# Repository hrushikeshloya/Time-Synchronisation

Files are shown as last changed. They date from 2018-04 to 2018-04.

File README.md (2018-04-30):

# EDL-TimeSync
Public Repository of our Electronic Design Lab Project Time Synchronization in Vibration Sensors under Prof. M.C. Chandorkar

Members:
1. Hrushikesh Loya (150010017@iitb.ac.in)
2. Rajat Patel (150010002@iitb.ac.in)
3. Yashswi Jain (150110039@iitb.ac.in)

### About

The project attempts to build a customizable skeleton which can be used to synchronise multiple sensors to take time stamped readings and transmit it to the user. 

We have developed a skeleton that can accommodate two vibration sensors (MMA7361, in our case) mounted on two self-designed and realised peripheral microcontrollers with ATMEGA-328P and a customised central Microprocessor for collecting the sampled and stamped data from both of them and sending them them to the UNIX PC for further analysis. 

### Board Design

You can find the eagle schematic and board files for both the central and peripheral microcontroller in Board Design folder.

### Communication Protocols

#### Mode 1 (CSS)
Continuous Sampling and Sending: The sampled data is sent to PC by each of the two Local Microprocessors alternatively. The sampling is done through interrupts and time spent in each interrupt service routine as mentioned above is 35 microseconds. This doesn’t affect the transmission as ATMEGA328p has 64 byte buffer for Serial transmission.
Maximum Attainable sampling rate: 2.5KHz

#### Mode 2 (Burst Mode)
Sampling till buffer is full and then sending in a burst: In this method we sample the data till the buffer is full and then send the data from 2 Local Microprocessors to the PC alternatively. The sampling of Data is stopped when the data is transmitted to PC. The sampling starts only after both the Local Microprocessors are done with the transmission.
Maximum Attainable sampling rate: 25KHz

### Time Synchronization

As the two peripheral microcontrollers have different clocks, there will be drifts in both the clocks after some time. To match the sampling instants, we use the same square wave which we sent from central for alternate data sending.

If there is drift in clocks, the timer1 (inbuilt timer in Atmega328P) values will not be same. So after certain number of cycles of square wave we set the the timer1 values of both the  microprocessors to initial values. And we send the timestamp when the synchronization is done to PC from Central Microprocessor. This way we acheive synchronized data.

### Firmware

##### How to upload the code?
Use Arduino IDE, to compile and upload the code. central.ino corresponds to central microprocessor, interrupt_transmit.ino corresponds to first peripheral, and interrupt_transmit2.ino corresponds to second peripheral.

##### Aquiring Serial Data on PC?
We use picocom (sudo apt-get install picocom) to aquire the serial data on ubuntu based PC. 
sudo picocom -b 230400 /dev/ttyUSB0 | tee logfile  (check your port on which arduino is connected, our case it was /dev/ttyUSB0)  saves the data from the serial port of the computer to a log file named logfile.

##### Plotting and Interpretting the data?
The data we recieve is in byte format.
You can then use log_reader_v1.py and log_reader_v2.py to plot the data aquired without time sync and with timesync respectively.

### Results

You can have a view of few of the amazing results (with their log files) we have obtained in the Results folder

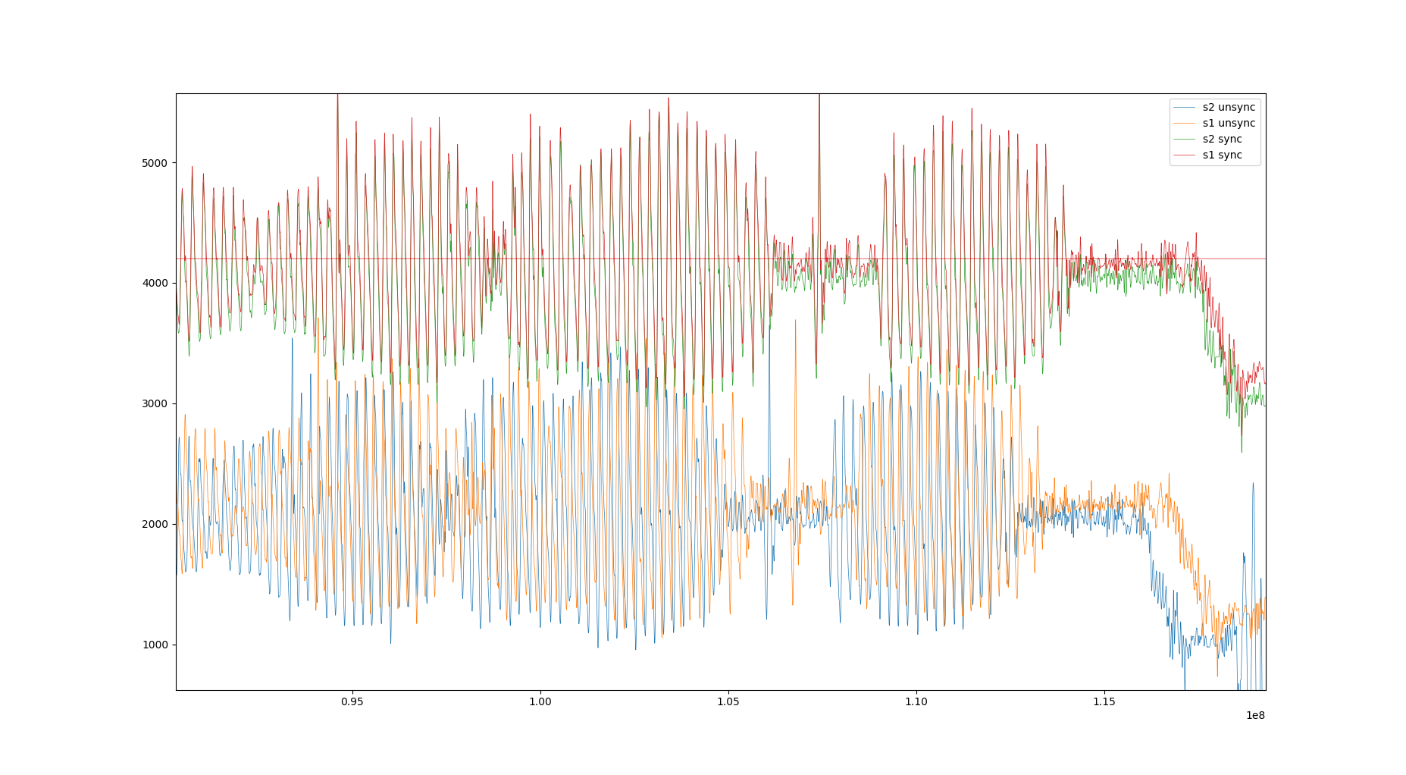
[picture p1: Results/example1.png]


Link to our complete report: https://docs.google.com/document/d/1JRsnFTGfe37P0LFT0vE4qM5fWR5oT6ynj_dwdIWIZMQ/edit?usp=sharing

Link to the final presenentation: https://docs.google.com/presentation/d/1-vB_suMupCKIn_ZJjNBb9ri4n2t6BEERArDRMrE7F0k/edit?usp=sharing

Refrences: 

1. "Time synchronization of a wired sensor network for structural health monitoring":  http://iopscience.iop.org/article/10.1088/0964-1726/17/01/015016

Chalte Hai!

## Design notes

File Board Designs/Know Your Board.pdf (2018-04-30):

# P_P- Peripheral & P_P - Central

### 1. Powering Up

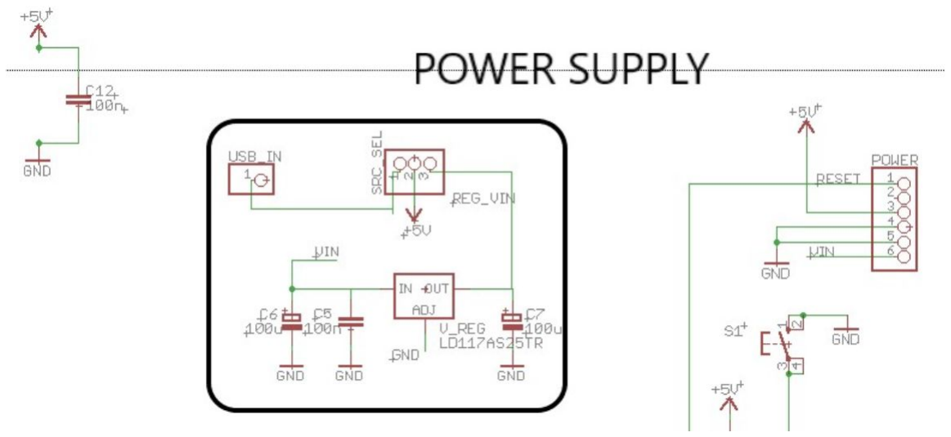
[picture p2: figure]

In the Figure above, the 6X1 pin-head on the right corner is the Power Section of the board. V-In and +5V pins can be found here.

The Board has a dual channel powering mechanism.
- Using the USB_VCC : If you plan to use your peripheral attached with a FTDI module which is capable of harnessing the USB_VCC then all you need to do is plug in the USB_VCC directly into any of the +5V pins on the board to power it up.
- Using External Power Supply : The board can also be powered
externally by a 10V DC | supply. The Input can be given to the V-IN | pin
in power section of the board and the Regulated 5V output (REG_VIN) has to be connected to +5V pin manually with a jumper.
For regulating the voltage, the board houses a LD1117 LDO voltage regulator at its heart.

Checking the power supply:
Power up the board using any one of the two sources as described above. If everything is correct, A RED LED will start glowing. This indicates that the Power unit of the Board is working fine.

### 2. Atmega 328P Pins at your Disposal

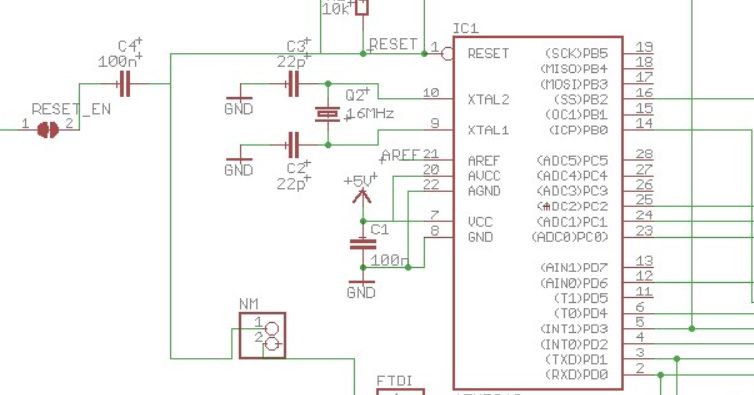
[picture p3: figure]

| The Board houses a 16MHz | crystal oscillator. With an appropriate prescaling factor(We
have used a factor of 4). At this prescaling factor, a max sampling frequency of around 320 KHz can be attained using the board.

The figure shows the Accelerometer of the board. This can be used to interface the board with a MMA7361 Triple - Axis accelerometer. (Its a P_P-Peripheral ONLY feature)

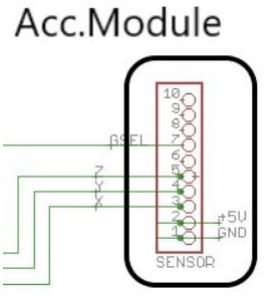
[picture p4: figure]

For detailed pin layout please refer to the Peripheral2.sch file.

CAUTION: It hasn’t been shown in the figure or the Schematic but the updated version of the board also comprises pins for Self-test, sleep and Sensitivity select. It should be clear from the labelling of the pins on the board.

FTDI Interfacing:

The figure shows the Pin head which can be used for interfacing the FTDI module.

ATTENTION: The NM pinhead has to be left unconnected!

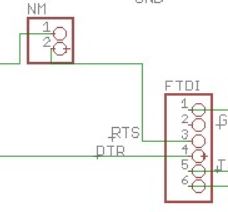
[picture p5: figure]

Communication Pins:

- P_P-Central

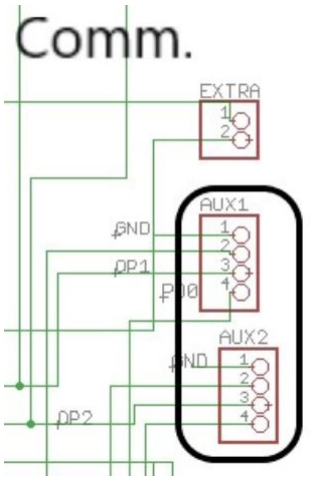
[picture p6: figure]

The figure shows the Communication front of the central microprocessor.
The EXTRA titled pinhead lets the user the freedom to use 1 analog and 1 digital pin by his own will(Unassigned pins)

AUX1 and AUX2 respectively is used for communicating with the auxiliary microprocessors. Each comprises of a GND pin, RX-TX pins and one digital pin.

OP1 - Atmega PIN 12 (dig.)
OP2 - Atmega PIN 6 (dig.)

- P_P- Peripheral:

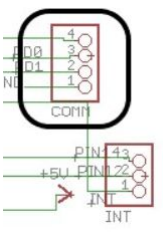
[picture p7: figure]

The figure shows the pinhead for communication with
the central microprocessor.
The COMM. pinhead is used for communication. The INT. pinhead houses 3 extra digital pins if required. (atmega pin 4,12,14).

The COMM. Pinhead comprises of RX,TX pins, 1 Dig. Pin (Pin 5 of ATMEGA), and GND. pin

Switches:

Both the boards have two switches each. One of them is used for resetting the microcontroller and the other is used for giving a high pulse at one of the digital pins of the atmega.

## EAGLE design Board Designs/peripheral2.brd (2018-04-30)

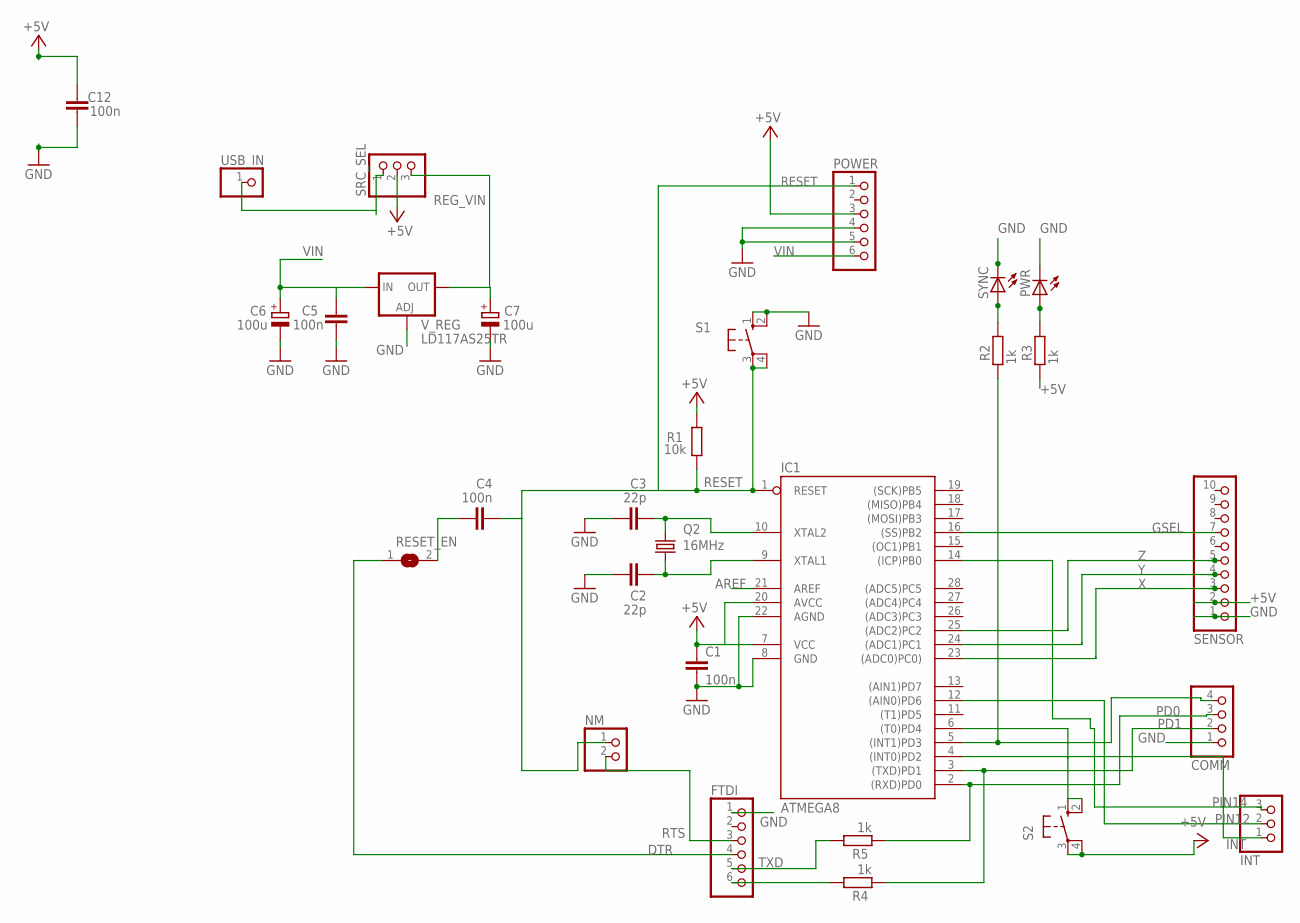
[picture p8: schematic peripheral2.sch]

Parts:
C1, C4, C5, C12: 100n; C1206
C2, C3: 22p; C1206
C6, C7: 100u; PANASONIC_D
COMM: PINHD-1X4; 1X04
FTDI: PINHD-1X6; 1X06
IC1: ATMEGA8; DIL28-3
INT: PINHD-1X3; 1X03
NM: PINHD-1X2; 1X02
POWER: PINHD-1X6; 1X06
PWR: LEDCHIPLED_1206; CHIPLED_1206
Q2: 16MHz; HC49/S
R1: 10k; R1206
R2, R3, R4, R5: 1k; R1206
RESET_EN: SJ
S1, S2: 10-XX; B3F-10XX
SENSOR: PINHD-1X10; 1X10
SRC_SEL: PINHD-1X3; 1X03
SYNC: LEDCHIPLED_1206; CHIPLED_1206
USB_IN: PINHD-1X1; 1X01
V_REG: LD117AS25TR; SOT223

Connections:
+5V: C1.1, C12.2, IC1.7 (VCC), IC1.20 (AVCC), POWER.3, R1.2, R3.2, S2.3, S2.4 (P1), SENSOR.2, SRC_SEL.2
A3: COMM.4, IC1.5 ((INT1)PD3), R2.2
AREF: IC1.21 (AREF)
DTR: FTDI.4, RESET_EN.1
GND: C1.2, C2.1, C3.1, C5.1, C6.-, C7.-, C12.1, COMM.1, FTDI.1, IC1.8 (GND), IC1.22 (AGND), POWER.4, POWER.5, PWR.C, S1.1 (S), S1.2 (S1), SENSOR.1, SYNC.C, V_REG.1 (ADJ)
GSEL: IC1.16 ((SS)PB2), SENSOR.7
INT: IC1.4 ((INT0)PD2), INT.1
unnamed: R2.1, SYNC.A
unnamed: PWR.A, R3.1
unnamed: FTDI.6, R4.1
unnamed: C2.2, IC1.9 (XTAL1), Q2.1
unnamed: C3.2, IC1.10 (XTAL2), Q2.2
unnamed: IC1.6 ((T0)PD4), S2.1 (S), S2.2 (S1)
unnamed: C4.1, RESET_EN.2
PD0: COMM.3, IC1.2 ((RXD)PD0), R5.2
PD1: COMM.2, IC1.3 ((TXD)PD1), R4.2
PIN12: IC1.12 ((AIN0)PD6), INT.2
PIN14: IC1.14 ((ICP)PB0), INT.3
REG_VIN: C7.+, SRC_SEL.3, V_REG.4 (OUT)
RESET: C4.2, IC1.1 (RESET), NM.1, POWER.1, R1.1, S1.3, S1.4 (P1)
RTS: FTDI.3, NM.2
TXD: FTDI.5, R5.1
USB_VCC: SRC_SEL.1, USB_IN.1
VIN: C5.2, C6.+, POWER.6, V_REG.3 (IN)
X: IC1.23 ((ADC0)PC0)), SENSOR.3
Y: IC1.24 ((ADC1)PC1), SENSOR.4
Z: IC1.25 ((ADC2)PC2), SENSOR.5

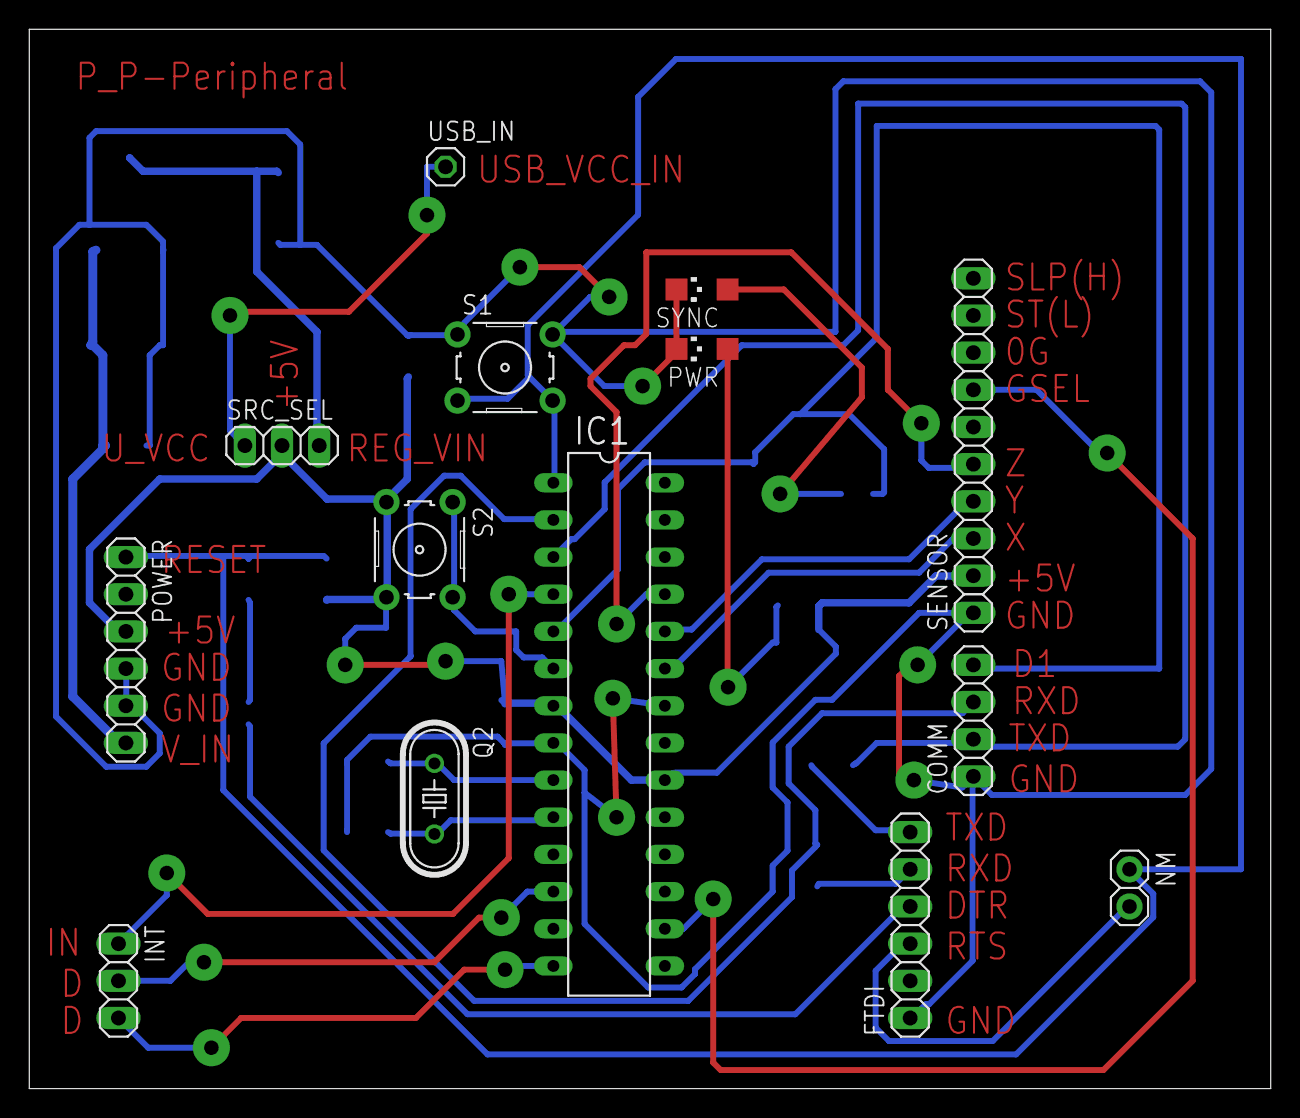
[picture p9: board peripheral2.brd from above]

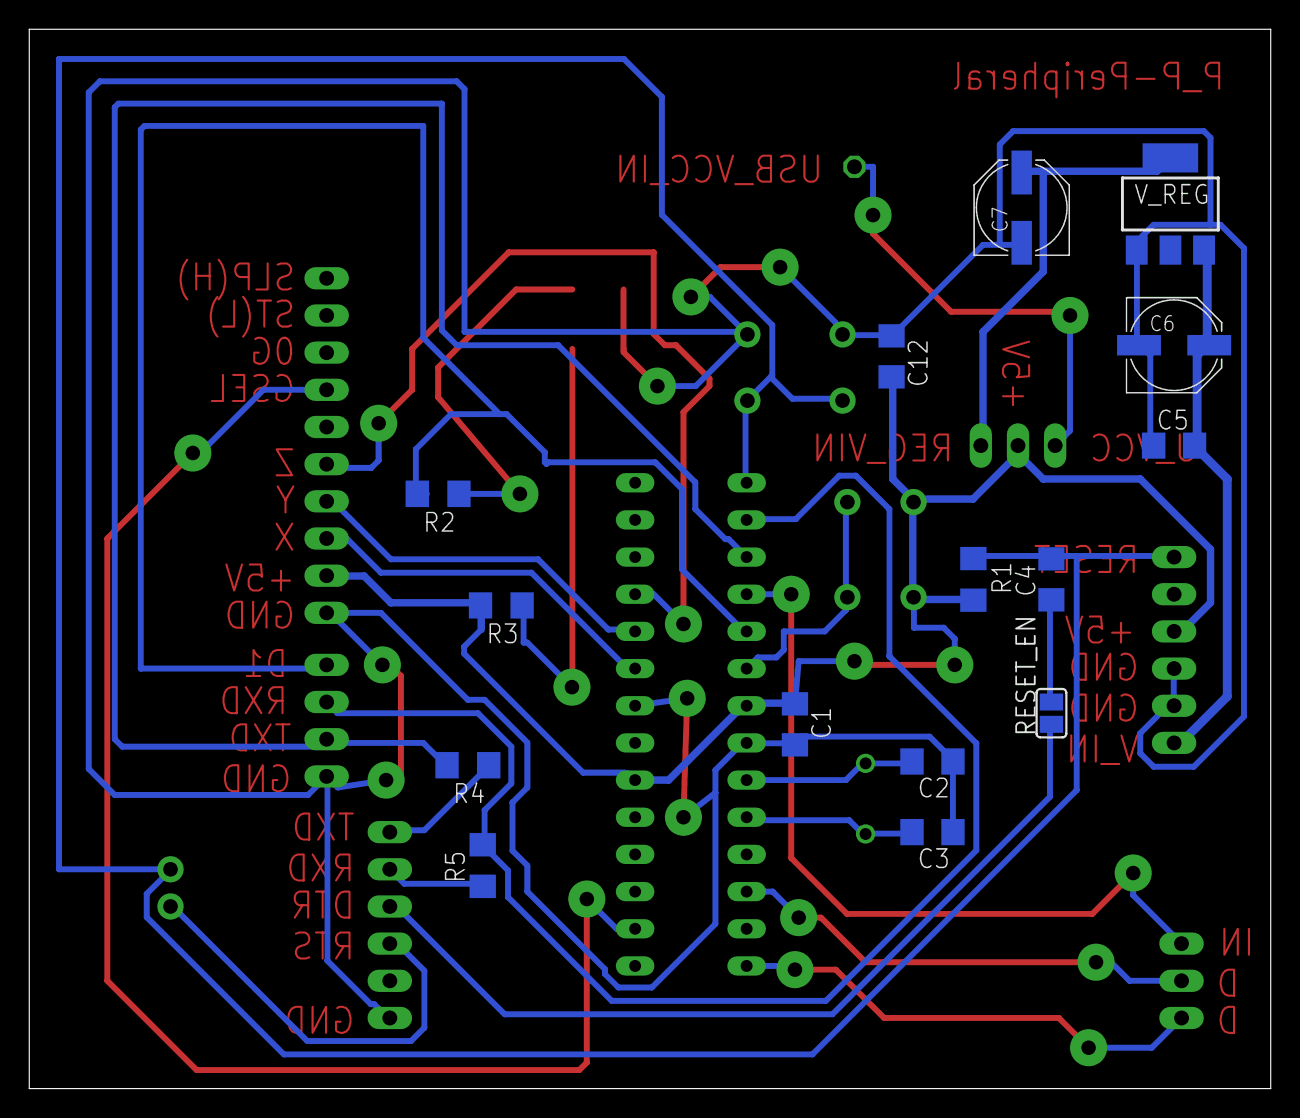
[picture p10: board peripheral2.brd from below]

Board: 2 copper layers, 84.8 x 72.4 mm, 29 parts (15 on the bottom side), 26 nets.

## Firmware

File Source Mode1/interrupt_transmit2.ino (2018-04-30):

#ifndef AcceleroMMA7361_h
#define AcceleroMMA7361_h
#define cbi(sfr, bit) (_SFR_BYTE(sfr) &= ~_BV(bit))
#define sbi(sfr, bit) (_SFR_BYTE(sfr) |= _BV(bit))
#if defined(ARDUINO) && ARDUINO >= 100
#include <Arduino.h>
#else
#include <WProgram.h>
#include <pins_arduino.h>
#endif

class AcceleroMMA7361
{
  public:
    AcceleroMMA7361();
    void begin();
    void begin(int sleepPin, int selfTestPin, int zeroGPin, int gSelectPin, int xPin, int yPin, int zPin);
    int getXRaw();
    int getYRaw();
    int getZRaw();
    int getXVolt();
    int getYVolt();
    int getZVolt();
    int getXAccel();
    int getYAccel();
    int getZAccel();
    void getAccelXYZ(int *_XAxis, int *_YAxis, int *_ZAxis);
    int getTotalVector();
    void setOffSets(int xOffSet, int yOffSet, int zOffSet);
    void calibrate();                             // only to be executed when Z-axis is oriented to the ground
// it calculates the offset values by assuming  Z = +1 G ; X and Y  = 0 G
    void setARefVoltage(double _refV);
    void setAveraging(int avg);
    int getOrientation();
    void setSensitivity(boolean sensi);
    void sleep();
    void wake();
    int _mapMMA7361V(int value);
    int _mapMMA7361G(int value);
        int _offSets[3];

  private:

    int _sleepPin;
    int _selfTestPin;
    int _zeroGPin;
    int _gSelectPin;
    int _xPin;
    int _yPin;
    int _zPin;

    int _polarities[3];
    double _refVoltage;
    int _average;
    boolean _sleep;
    boolean _sensi;
};
#endif



// acceleroMMA7361.h - Library for retrieving data from the MMA7361 accelerometer. 
// Copyright 2011-2012 Jef Neefs (neefs@gmail.com) and Jeroen Doggen (jeroendoggen@gmail.com)
// For more information: variable declaration, changelog,... see AcceleroMMA7361.h 
//
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
/// acceleroMMA7361.cpp - Library for retrieving data from the MMA7361 accelerometer.
/// For more information: variable declaration, changelog,... see AcceleroMMA7361.h


/// constructor
AcceleroMMA7361::AcceleroMMA7361()
{
    _sleepPin=0;
    _selfTestPin=0;
    _zeroGPin=0;
    _gSelectPin=0;
    _xPin=0;
    _yPin=0;
    _zPin=0;
    _offSets[0]=0;
    _offSets[1]=0;
    _offSets[2]=0;
    _polarities[0]=0;
    _polarities[1]=0;
    _polarities[2]=0;
    _refVoltage=0;
    _average=0;
    _sleep=false;
    _sensi=false;
}

/// begin function to set pins: sleepPin = 13, selfTestPin = 12, zeroGPin = 11, gSelectPin = 10, xPin = A0, yPin = A1, zPin = A2.
/// When you use begin() with an empty parameter list, these standard values are used
void AcceleroMMA7361::begin()
{
  begin(13, 12, 11, 10, A0, A1, A2);
}

/// begin variables
/// - int sleepPin: number indicating to which pin the sleep port is attached. DIGITAL OUT
/// - int selfTestPin: number indicating to which pin the selftest port is attached. DIGITAL OUT
/// - int zeroGPin: number indicating to which pin the ZeroGpin is connected to. DIGITAL IN
/// - int gSelectPin: number indication to which pin the Gselect is connected to. DIGITAL OUT
/// - int xPin: number indicating to which pin the x-axis pin is connected to. ANALOG IN
/// - int yPin: number indicating to which pin the y-axis  pin is connected to. ANALOG IN
/// - int zPin: number indicating to which pin the z-axis  pin is connected to. ANALOG IN
/// - int offset: array indicating the G offset on the x,y and z-axis
/// When you use begin() without variables standard values are loaded: A0,A1,A2 as input for X,Y,Z and digital pins 13,12,11,10 for sleep, selftest, zeroG and gSelect
void AcceleroMMA7361::begin(int sleepPin, int selfTestPin, int zeroGPin, int gSelectPin, int xPin, int yPin, int zPin)
{
  pinMode(sleepPin, OUTPUT);
  pinMode(selfTestPin, OUTPUT);
  pinMode(zeroGPin, INPUT);
  pinMode(gSelectPin, OUTPUT);
  pinMode(xPin, INPUT);
  pinMode(yPin, INPUT);
  pinMode(zPin, INPUT);
  digitalWrite(sleepPin,HIGH);
  digitalWrite(selfTestPin,LOW);
  _sleepPin = sleepPin;
  _selfTestPin = selfTestPin;
  _zeroGPin = zeroGPin;
  _gSelectPin = gSelectPin;
  _xPin = xPin;
  _yPin = yPin;
  _zPin = zPin;
  _sleep = false;
  setOffSets(0,0,0);
  setARefVoltage(5);
  setAveraging(10);
  setSensitivity(HIGH);
}

/// setOffSets( int offSetX, int offSetY, int offSetZ): Sets the offset values for the x,y,z axis.
/// The parameters are the offsets expressed in G-force (100 = 1 G)
/// Offsets are added to the raw datafunctions
void AcceleroMMA7361::setOffSets(int xOffSet, int yOffSet, int zOffSet)
{
  if (_refVoltage==3.3)
  {
    _offSets[0]= map(xOffSet,0,3300,0,1024);
    _offSets[1]= map(yOffSet,0,3300,0,1024);
    _offSets[2]= map(zOffSet,0,3300,0,1024);
  }
  else
  {
    _offSets[0]= map(xOffSet,0,5000,0,1024);
    _offSets[1]= map(yOffSet,0,5000,0,1024);
    _offSets[2]= map(zOffSet,0,5000,0,1024);
  }
}

/// setARefVoltage(double _refV): Sets the AREF voltage to external, (now only takes 3.3 or 5 as parameter)
/// default is 5 when no AREF is used. When you want to use 3.3 AREF, put a wire between the AREF pin and the
/// 3.3 V VCC pin. This increases accuracy
void AcceleroMMA7361::setARefVoltage(double refV)
{
  _refVoltage = refV;
  if (refV == 3.3)
  {
    analogReference(EXTERNAL);
  }
}

/// setAveraging(int avg): Sets how many samples have to be averaged in getAccel default is 10.
void AcceleroMMA7361::setAveraging(int avg)
{
  _average = avg;
}

/// setSensitivity sets the sensitivity to +/-1.5 G (HIGH) or +/-6 G (LOW) using a boolean HIGH (1.5 G) or LOW (6 G)
void AcceleroMMA7361::setSensitivity(boolean sensi)
{
  _sensi = sensi;
  digitalWrite(_gSelectPin, !sensi);
}

/// sleep lets the device sleep (when device is sleeping already this does nothing)
void AcceleroMMA7361::sleep()
{
  if (!_sleep)
  {
    digitalWrite(_sleepPin, LOW);
    _sleep = true;
  }
}

/// wake enables the device after sleep (when device is not sleeping this does nothing) there is a 2 ms delay, due to enable response time (datasheet: typ 0.5 ms, max 2 ms)
void AcceleroMMA7361::wake()
{
  if (_sleep == true)
  {
    digitalWrite(_sleepPin, HIGH);
    _sleep = false;
    delay(2);
  }
}

/// getXRaw(): Returns the raw data from the X-axis analog I/O port of the Arduino as an integer
int AcceleroMMA7361::getXRaw()
{
  return analogRead(_xPin)+_offSets[0]+2;
}

/// getYRaw(): Returns the raw data from the Y-axis analog I/O port of the Arduino as an integer
int AcceleroMMA7361::getYRaw()
{
  return analogRead(_yPin)+_offSets[1]+2;
}

/// getZRaw(): Returns the raw data from the Z-axis analog I/O port of the Arduino as an integer
int AcceleroMMA7361::getZRaw()
{
  return analogRead(_zPin)+_offSets[2];
}

/// getXVolt(): Returns the voltage in mV from the X-axis analog I/O port of the Arduino as a integer
int AcceleroMMA7361::getXVolt()
{
  return _mapMMA7361V(getXRaw());
}

/// getYVolt(): Returns the voltage in mV from the Y-axis analog I/O port of the Arduino as a integer
int AcceleroMMA7361::getYVolt()
{
  return _mapMMA7361V(getYRaw());
}

/// getZVolt(): Returns the voltage in mV from the Z-axis analog I/O port of the Arduino as a integer
int AcceleroMMA7361::getZVolt()
{
  return _mapMMA7361V(getZRaw());
}

/// getXAccel(): Returns the acceleration of the X-axis as a int (1 G = 100.00)
int AcceleroMMA7361::getXAccel()
{
   return _mapMMA7361G(getXRaw());
}

/// getYAccel(): Returns the acceleration of the Y-axis as a int (1 G = 100.00)
int AcceleroMMA7361::getYAccel()
{
  
  return _mapMMA7361G(getYRaw());
}

/// getZAccel(): Returns the acceleration of the Z-axis as a int (1 G = 100.00)
int AcceleroMMA7361::getZAccel()
{
 return _mapMMA7361G(getZRaw());
}

/// getAccelXYZ(int *_XAxis, int *_YAxis, int *_ZAxis) returns all axis at once as pointers
void AcceleroMMA7361::getAccelXYZ(int *_XAxis, int *_YAxis, int *_ZAxis)
{
  int sum[3];
  sum[0] = 0;
  sum[1] = 0;
  sum[2] = 0;
  for (int i = 0;i<_average;i++)
  {
    sum[0] = sum[0] + _mapMMA7361G(getXRaw());
    sum[1] = sum[1] + _mapMMA7361G(getYRaw());
    sum[2] = sum[2] + _mapMMA7361G(getZRaw());
  }
  *_XAxis = sum[0]/_average;
  *_YAxis = sum[1]/_average;
  *_ZAxis = sum[2]/_average;
}

/// mapMMA7361V: calculates and returns the voltage value derived from the raw data. Used in getXVoltage, getYVoltage, getZVoltage
int AcceleroMMA7361::_mapMMA7361V(int value)
{
  if (_refVoltage==3.3)
  {
    return map(value,0,1024,0,3300);
  }
  else
  {
    return map(value,0,1024,0,5000);
  }
}

/// mapMMA7361G: calculates and returns the accelerometer value in degrees derived from the raw data. Used in getXAccel, getYAccel, getZAccel
int AcceleroMMA7361::_mapMMA7361G(int value)
{
  if(_sensi == false)
  {
    if (_refVoltage==3.3)
    {
      return map(value,0,1024,-825,800);
    }
    else
    {
      return map(value,0,1024,-800,1600);
    }
  }
  else
  {
    if (_refVoltage==3.3)
    {
      return map(value,0,1024,-206,206);
    }
    else
    {
      return map(value,0,1024,-260,419);
    }
  }
}

/// calibrate(): Sets X and Y values via setOffsets to zero. The Z axis will be set to 100 = 1G
/// WARNING WHEN CALIBRATED YOU HAVE TO MAKE SURE THE Z-AXIS IS PERPENDICULAR WITH THE EARTHS SURFACE
void AcceleroMMA7361::calibrate()
{
  Serial.println(getOrientation());
  Serial.print("\nCalibrating MMA7361011");
  double var = 5000;
  double sumX = 0;
  double sumY = 0;
  double sumZ = 0;
  for (int i = 0;i<var;i++)
  {
    sumX = sumX + getXVolt();
    sumY = sumY + getYVolt();
    sumZ = sumZ + getZVolt();
    if (i%100 == 0)
    {
      Serial.print(".");
    }
  }
  if (_sensi == false)
  {
    setOffSets(1672 - sumX / var,1671 - sumY / var, + 1876 - sumZ / var);
  }
  else
  {
    setOffSets(1650 - sumX / var,1650 - sumY / var, + 2450 - sumZ / var);
  }
  if (abs(getOrientation())!=3)
  {
    Serial.print("\nunable to calibrate");
    setOffSets(0,0,0);
  }
  else
  {
    Serial.print("\nDONE");
  }
}

/// getOrientation returns which axis perpendicular with the earths surface x=1,y=2,z=3 is positive or
/// negative depending on which side of the axis is pointing downwards
int AcceleroMMA7361::getOrientation()
{
  int gemiddelde = 10;
  int x = 0;
  int y = 0;
  int z = 0;
  int xAbs = 0;
  int yAbs = 0;
  int zAbs = 0;
  for(int i = 0; i<gemiddelde ; i++)              //We take in this case 10 measurements to average the error a little bit
  {
    x = x+getXAccel();
    y = y+getYAccel();
    z = z+getZAccel();
  }
  x= x/gemiddelde;
  y = y/gemiddelde;
  z = z/gemiddelde;
  xAbs = abs(100-abs(x));
  yAbs = abs(100-abs(y));
  zAbs = abs(100-abs(z));
  if (xAbs<yAbs&&xAbs<zAbs)
  {
    if (x>0)
    {
      return 1;
    }
    return -1;
    
  }
  if (yAbs<xAbs&&yAbs<zAbs)
  {
    if (y>0)
    {
      return 2;
    }
    return -2;
  }
  if (zAbs<xAbs&&zAbs<yAbs)
  {
    if (z>0)
    {
      return 3;
    }
    return -3;
  }
  return 0;
}

/// getTotalVector returns the magnitude of the total acceleration vector as an integer
int AcceleroMMA7361::getTotalVector()
{
  return sqrt(square(_mapMMA7361G(getXRaw())) + square(_mapMMA7361G(getYRaw())) + square(_mapMMA7361G(getZRaw())));
}
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
